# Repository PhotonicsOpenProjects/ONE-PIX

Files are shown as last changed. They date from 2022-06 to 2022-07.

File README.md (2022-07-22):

<p align="center">
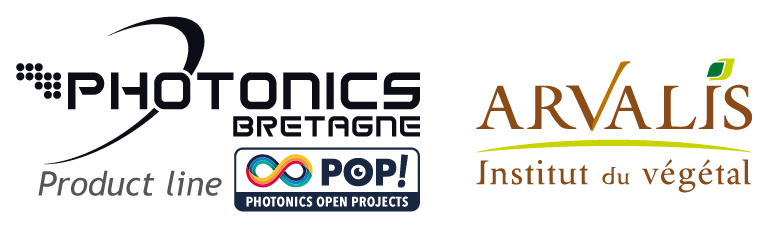
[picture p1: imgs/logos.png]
logos

</p>

# ONE-PIX kit project   #
## Introduction 

The ONE-PIX kit is an hyperspectral camera using single pixel imaging principle to measure hypercubes in the visible region. It can be enhanced towards the infrared region. This modular kit can be used with different spectrometers and optical elements for the collection. To date, it can measure scenes exposed to ambient light, but it has been primarily tested and developed for use in dimly lit indoor environments.

This kit is ideal for getting started with hyperspectral imaging or single pixel imaging. Thus it is a tool for teachers and students to discover non conventional imaging. It is also an economic tool to produce low cost hypercubes of tailored scenes or to reproduce academical results within the robotic vision field. 
To learn more about single pixel imaging theory used for hyperspectral imaging, you can read our [article. ](https://www.ncbi.nlm.nih.gov/pmc/articles/PMC7070961/)

This kit was developed with the primary need in mind to be able to be assembled on a standard fablab with laser cutting. Little wiring (all low voltage) and no soldering is required. You should find a fablab in your neighbourhood capable (and enthusiastic) of helping you build this cool instrument, especially if they can have some fun with it afterwards.

### Working principle

The ONE-PIX kit contains a video projector and a fibered spectrometer with superimposed fields of view. Both are connected and controlled by a Raspberry Pi board.
 
<p align="center">
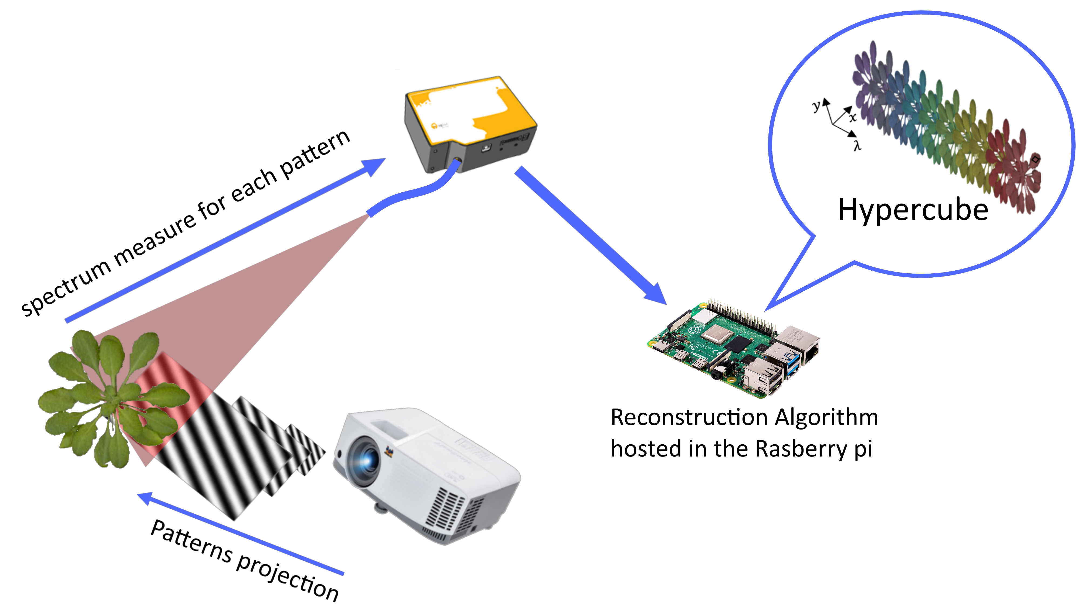
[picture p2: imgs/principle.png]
ONE-PIX principle

</p>

For more information about the single pixel imaging you can go [here](ONE-PIX_soft/doc/Single%20Pixel%20Imaging%20tutorial/Single%20Pixel%20Imaging.ipynb)

ONE-PIX technology involves projecting a series of patterns onto a scene to be imaged. A spectrometer measures the average reflected spectrum of the scene for each projection. An algorithm then reconstructs the hypercube of the scene from all the spectra measured during the acquisition. 
The Raspberry Pi board ensures the synchronization between patterns projections and the spectrometer measurements.
### Architecture of the ONE-PIX kit repository 

The ONE-PIX kit project contains two folders :

- A [hardware build folder](hardware_build) contains all the files and information to build a case containing all the components of the ONE-PIX kit and their 3D printed attachments.
- A [ONE-PIX Software folder](ONE-PIX_soft) contains the scripts and software embedded on the Raspberry Pi and all the information to install and use it properly. 
## Steps to produce one ONE-PIX kit

These followings steps are presented in chronological order to create a ONE-PIX kit. 

### Build your own hardware ONE-PIX kit

Every informations and files to build your own hardware kit are avalaible in the [hardware build folder](hardware_build)

<p align="center">
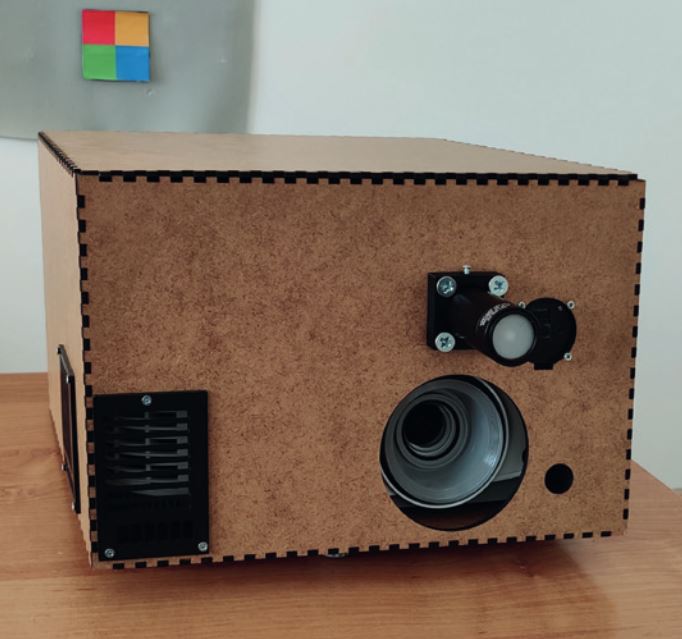
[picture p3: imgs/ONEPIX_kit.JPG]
ONE-PIX kit photo

</p>

This folder contains:

- The [material needed list](hardware_build/materials_needed.pdf) file containing raw materials and equipments needed to build the ONE-PIX kit hardware.
- The [hardware building tutorial](hardware_build/hardware_building_tutorial.pdf) file containing details steps to build the ONE-PIX kit.
- [STL files ready to 3D_printing](hardware_build/STL_file_ready_to_3D_printing) folder containing every files to 3D print components fixation parts of the kit.
- [plans of box sides ready to cut](hardware_build/plan_of_box_sides_ready_to_cut) folder containing every files to  laser cut sides of the ONE-PIX kit case.
- The [CAO files to modify hardware](hardware_build/CAO_files_to_modify_hardware) folder containting the complet CAO of the ONE-PIX kit if you want to adapt the hardware to your application.

> **_NOTE:_** You can also buy a premounted and adapted ONE-PIX kit [here](https://www.photonics-bretagne.com/fr/product/imageur-hyperspectral-one-pix-pop/). 
> Keep in mind that it is also the best way to help us maintaining the forge, integrating contribution and even propose one day industrial implementation of this technology for the broader audience and usage possible.

### Install ONE-PIX software on the Raspberry Pi 

To install the ONE-PIX kit software you need to follow steps discribed in [Readme installation](ONE-PIX_soft/README.md) before measuring hyperspectral images.
For troubleshooting in installation you can go to the [issue section](https://github.com/PhotonicsOpenProjects/ONE-PIX/issues)

###  Measuring and analysing hypercubes 

The software architecture of the ONE-PIX kit offers different ways to measure, reconstruct and analyze hyperspectral images. 

<p align="center">
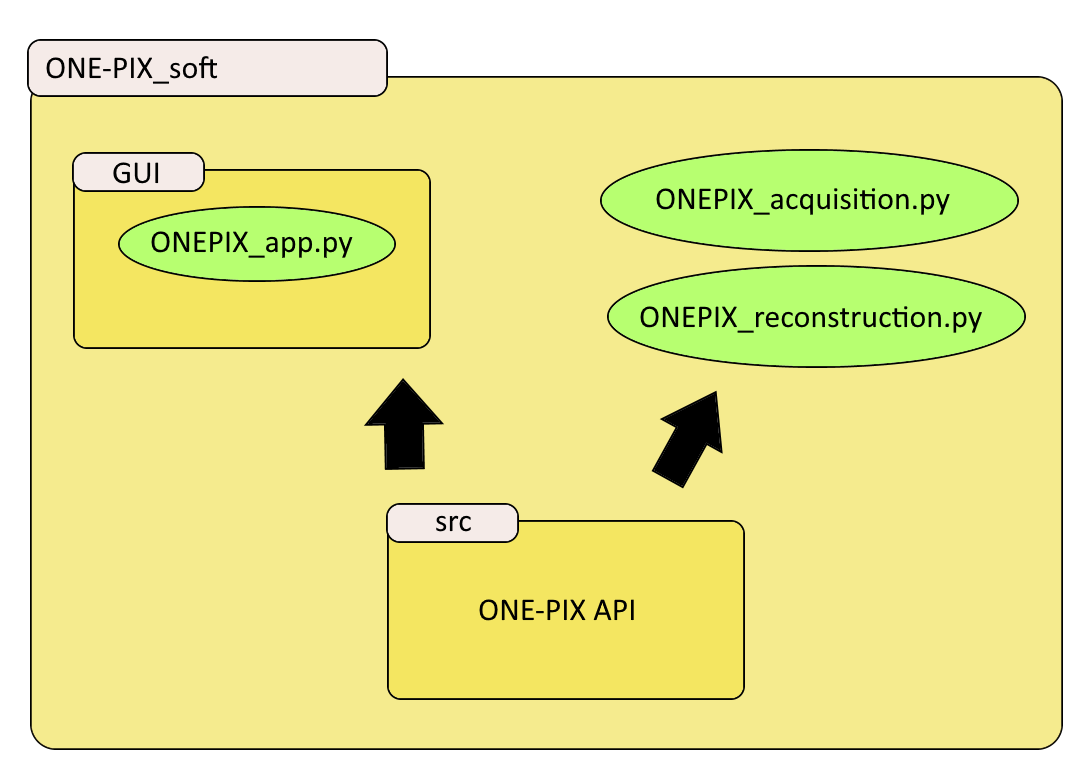
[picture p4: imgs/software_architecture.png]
ONE-PIX software architecture

</p>

- The fastest way to measure and analyze hyperspectral images is to use the [GUI interface](ONE-PIX_soft/doc/ONE-PIX_GUI_user_manual.pdf)
- For more advanced acquisitions,use directly ONEPIX_acquisition.py and ONEPIX_reconstruction.py [Python examples scripts](ONE-PIX_soft) and improve them with using the [API](https://one-pix.readthedocs.io/en/latest/introduction.html).
 
## Contributing 

### Mounting experience

If you use it from a already assemble kit, and do not found a detail on the manual, tell us !
If you assemble it by yourself and found some simpliest or smartest way to do it, please share !
If you encounter difficulties, have suggestions or even just cheers the developpers, do not hesitate again !

### Use Cases

Any questions, pedagogical or in a front of science, very applied or meta-conceptual are interesting for us and other users. A brief description and welcome message on this repository will be greatly apreciated. If we are curious enough we will contact you.

### New functions

As you will rapidly catch-it : this simple set-up has an infinity of potential developements, applications and usages. Feel free to play with it once it works at your place. 
If you find new tricks, feel free to share it with us and the community. We will dedicate ourselves (on the limits of our daily hours) to make the best effort to integrate and promote to the community every contribution with the greater respect to your credits. 

### Your version

If you tried a new sensors, an other mechanical plan, you can freely create your own forks but if you consider it could be usefull to keep consistency with other develepment and insturmental choice, we can discuss on intégrating also , spectormeter wrappers or even more crazy evolution in the main.

## Important remarks

:bulb: **Tip:** Do not forget to have fun... because we had some making it for you !

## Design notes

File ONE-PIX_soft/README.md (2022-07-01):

# Readme for the ONE-PIX software installation #
# Introduction 

The installation of the ONE-PIX software is achievable as the hardware installation is fully completed..
To do so, you can follow the [hardware building tutorial](/hardware_build/hardware_building_tutorial.pdf) .
You can also buy an already premounted ONE-PIX  kit [here](https://www.photonics-bretagne.com/fr/product/imageur-hyperspectral-one-pix-pop/)

This tutorial details all the steps required to install the ONE-PIX software on a Raspberry Pi 4 board. 

# Installing the Raspberry Pi OS on the SD card and remote control

We recommend to use The ONE-PIX with a remote control Desktop.It allow you to run long acquisition in a more automated way. 

<p align="center">
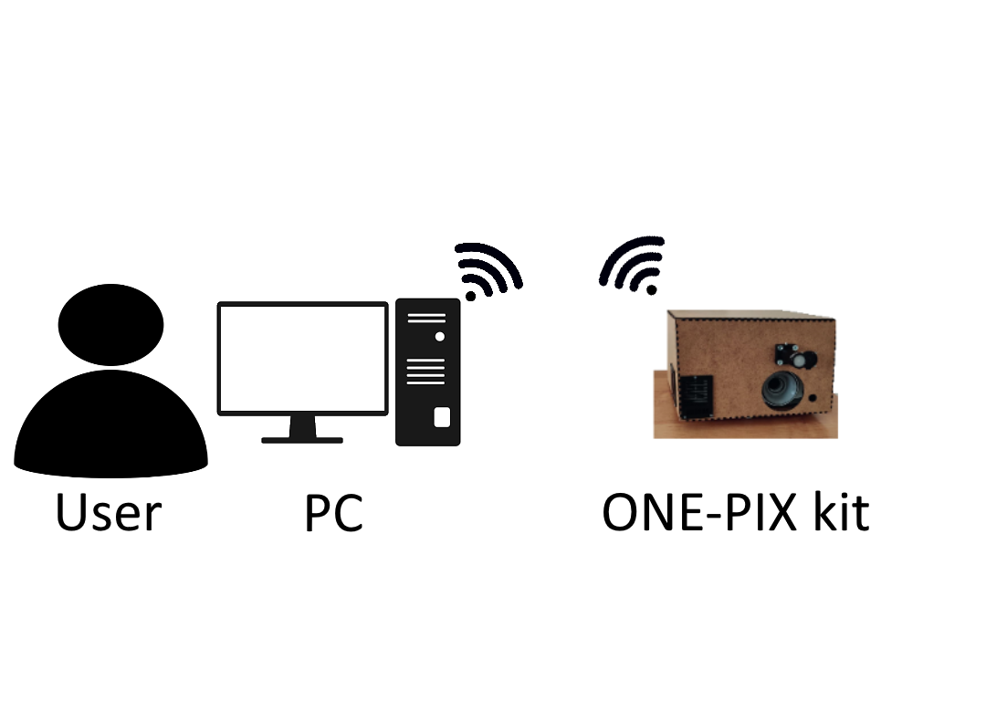
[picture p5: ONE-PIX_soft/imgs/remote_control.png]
remote control

</p>

Here we assume that The ONE-PIX soft was developed to use a raspberry pi with Raspbian OS.
However it possible use directly your PC with python for more advanced performance. 

To install the Raspbian OS on the SD card you can follow steps on this link [here](https://www.raspberrypi.org/documentation/installation/installing-images/ )

To remote control your raspberry pi you can follow this tutorial [here](https://www.realvnc.com/en/blog/how-to-setup-vnc-connect-raspberry-pi/#:~:text=You%20can%20even%20create%20and,will%20be%20able%20to%20connect. )

# ONE-PIX software installation 

## Download git repository

The first step of this installation is to clone the ONE-PIX directory from Github.

From the Raspberry Pi, open a terminal and go to the desktop with the following command line:

```
cd Desktop
```

Download the ONE-PIX software from git 

```
sudo git clone https://github.com/PhotonicsOpenProjects/ONE-PIX.git
```

## Requirements installation

A folder ONE-PIX _soft was created on the desktop.
with the terminal go in this folder 

```
cd Desktop/ONE-PIX/ONE-PIX_soft
```

You need to install Python packages to run ONE-PIX_soft. 
For that, just run the following command:

```
pip install -r requirements.txt
```

## Dependencies installation
More dependencies are requested to use OceanInsight spectrometers (Seabreeze) and the OpenCV library. 

Installing Seabreeze dependencies: 
```
sudo apt-get -y install libglu1
sudo apt-get -y install libaio1 libaio-dev
sudo apt-get -y install libglib2.0-0
sudo apt-get -y install libasound2
sudo apt-get -y install libusb-0.1-4
```

Installing OpenCV dependencies: 

```
sudo apt-get -y install build-essential cmake pkg-config
sudo apt -y install libjpeg-dev libtiff5-dev libjasper-dev libpng-dev
sudo apt -y install libavcodec-dev libavformat-dev libswscale-dev libv4l-dev
sudo apt -y install libxvidcore-dev libx264-dev
sudo apt -y install libfontconfig1-dev libcairo2-dev
sudo apt -y install libgdk-pixbuf2.0-dev libpango1.0-dev
sudo apt -y install libgtk2.0-dev libgtk-3-dev
sudo apt -y install libatlas-base-dev gfortran
sudo apt -y install libhdf5-dev libhdf5-serial-dev libhdf5-103
sudo apt -y install libqt5gui5 libqt5webkit5 libqt5test5 python3-pyqt5
sudo apt -y install python3-dev
```

## Spectrometer rules configuration
You need to configure USB rules to allow data tranferts from your spectrometer.

If the spectrometer used is this [list of tested spectrometer](../ONE-PIX_soft/doc/tested_spectrometers.pdf) follow steps for your model. 

Else, the spectrometer used is not in this list, you need to see [adding a new spectrometer](https://one-pix.readthedocs.io/en/latest/contributing.html#adding-a-new-spectrometer) API section.

### Ocean Insight spectrometers 

To configure Ocean Insight USB rules you need to copy the file the 10-oceanoptics.rules file stored in the [DLL folder](../ONE-PIX_soft/src/DLL) and paste it in the /etc/udev/rules.d folder of the Rapsberry pi.

For that go to the DLL folder

```
cd src/DLL
```

and copy/paste the 10-oceanoptics.rules in /etc/udev/rules.d folder with this command line:

```
sudo cp 10-oceanoptics.rules   /etc/udev/rules.d
```

### Avantes spectrometers

You need to update the /etc/udev/rules.d file of the raspberry pi to fix USB rules for Avantes Spectrometers.

To do so, go to this file with this command line: 
```
cd /etc/udev/rules.d
```
and add text in the file with these lines: 

```
sed -i '13 i SUBSYSTEM=="usb", ATTRS{idVendor}=="1992", ATTRS{idProduct}=="0667", MODE="0666"' 99-com.rules
sed -i '14 i SUBSYSTEM=="usb", ATTRS{idVendor}=="1992", ATTRS{idProduct}=="0668", MODE="0666"' 99-com.rules
sed -i '15 i SUBSYSTEM=="usb", ATTRS{idVendor}=="1992", ATTRS{idProduct}=="0669", MODE="0666"' 99-com.rules 

```
Finally, save and close the rules.d file.

## Activate Raspberry Pi camera 

to use ONE-PIX kit you need to activate the raspberry pi camera  for that go 

Enable SSH,VNC and the camera 

<p align="center">
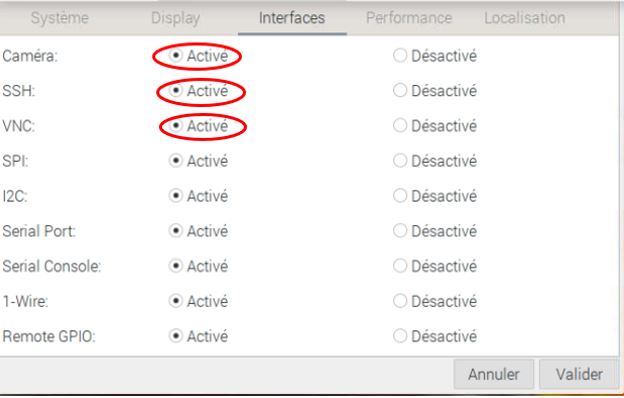
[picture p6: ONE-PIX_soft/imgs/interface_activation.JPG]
interface activation

</p>

## Dual screen configuration
In order to perform ONE-PIX  measurements, it is necessary to set up a second screen dedicated to displaying the patterns to be projected on your scenes.
 
You need to change the boot/config.txt file of the Raspberry Pi to force the double screen stored in DLL folder. 
You need to supress your existing boot/config.txt and replace it by  preconfiguring config file stored in the[DLL folder](../ONE-PIX _soft/src/DLL).
For that use these command lines : 
```
sudo rm /boot/config.txt
sudo cp config.txt /boot
```
# Finalisation and checking of the installation

First, shutdown the Raspberry Pi and replug in the hardware benchtop. 
Then, plug the mini HDMI on the HDMI1 port.  
Power on the projector and the Raspebrry Pi board. 
Remote control your Pi with your computer.

Now, you need to configure screen display. For that, go in the screen configuration menu:

<p align="center">
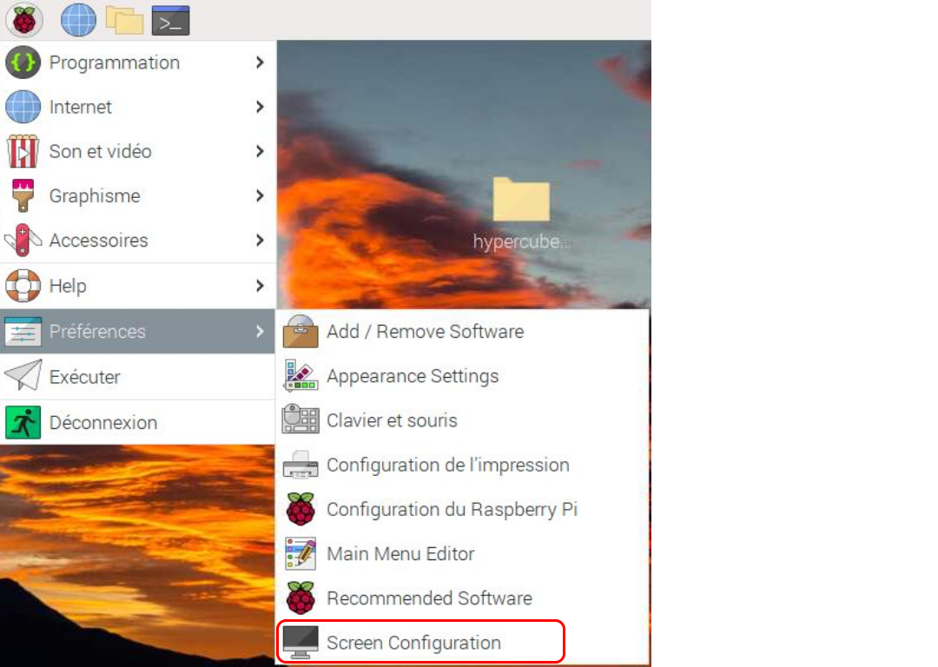
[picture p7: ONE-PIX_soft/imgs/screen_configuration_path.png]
screen configuration menu path

</p>

This window will pop up:

<p align="center">
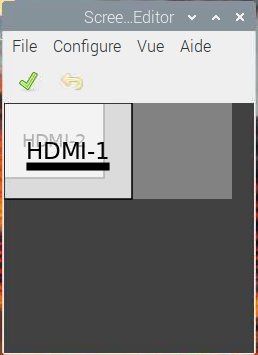
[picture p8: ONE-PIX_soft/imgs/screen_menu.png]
screen configuration menu

</p>

The HDMI1 and HDMI2 are superimposed. You need to grab HMDI 2 at the right of HDMI 1 with the mouse. 

<p align="center">
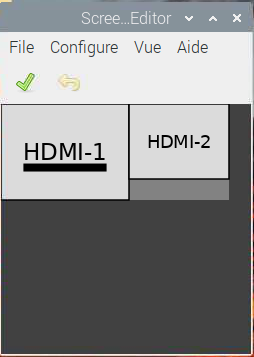
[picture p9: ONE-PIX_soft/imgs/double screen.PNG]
double screen

</p>

Now with VNC Viewer you can see two screens. The first one is the screen of the Raspberry
Pi desktop and the second is the screen of the projector. 

set the resolution of the screen 1 with 1024x768 pix and the screen 2 in 600x800pix. 

click one the green ticks to validate changes.

:warning: **Warning:** For long acquisition it may be necessary to deactivate the sleepmode. you can follow this [tutorial](https://pimylifeup.com/raspberry-pi-screensaver/)

<p align="center">
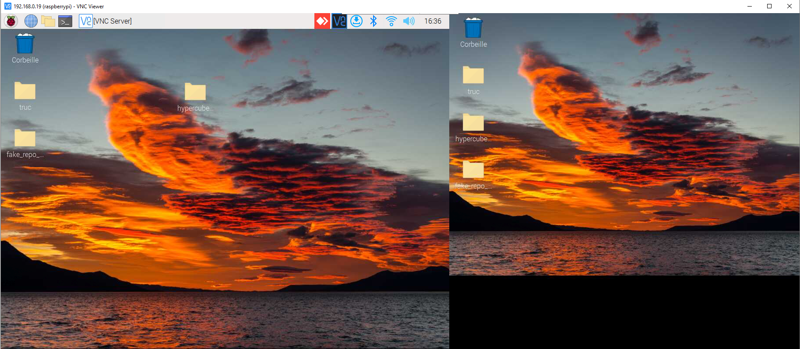
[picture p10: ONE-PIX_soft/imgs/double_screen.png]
vnc vnc viewer double screen

</p>

The installation is now complete. 
Now you can follow the [tutorial measure hyperspectral image](/ONE-PIX_soft/doc/tutorial_measure_hyperspectral_image.pdf) to measure your first hyperspectral datacube !

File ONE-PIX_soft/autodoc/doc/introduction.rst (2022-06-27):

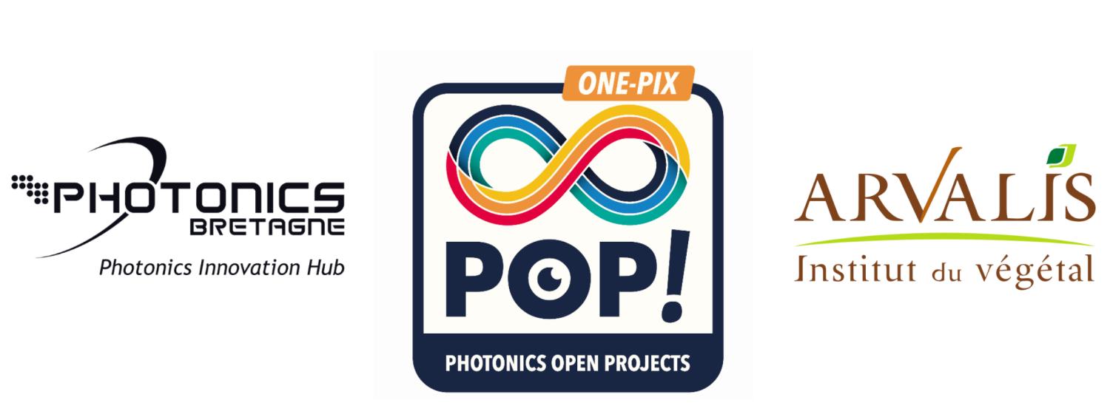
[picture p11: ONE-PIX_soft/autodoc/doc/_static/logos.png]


============
Introduction
============

The ONE-PIX kit is a low-cost single-pixel hyperspectral imaging education kit. This module is fully available on Github (see `here <https://github.com/IanHarvey/bluepy/>`_)
The current implementation has been developed in Python 3 and tested on a Raspberry Pi 4 8 Go, running Raspbian 11 (bullseye), but should also work with Windows or Ubuntu on most computers.

Motivations
------------
As the various spectral imaging technologies are relatively very expensive, we want to popularise the use of these new cutting-edge technologies. Thus, this kit aims to allow anyone to design their own kit or to order one from Photonics Bretagne.
As this research topic remains very broad, a Github repository allows to share all the contributions made within a community dedicated to single-pixel hyperspectral imaging.

This package is intended to provide:
--------------------------------------------

- Python scripts for interfacing the kit.
- Acquisitions and reconstructions scripts implementing various compressed imaging methods 
- Analysis tools to make use of the measured datacubes 



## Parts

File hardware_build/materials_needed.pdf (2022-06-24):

Type of item | item | quantity | comments
Component | Modified PA503S viewsonic videoprojector | 1 | For an optimal performance the hspi kit need a video projector with a modified optical chain. You can contact us to buy one here. (https://www.photonics-bretagne.com/en/perfos-rto/products/services/)
| Rasbperry pi 4B+ (8Go Ram) model | 1
| micro SD card 64 Go with SD adaptator | 1
| USB key | 1
| Raspberry pi camera | 1
| Optical fiber | 1
| SM1 thorlabs tube | 1
| Divergent lens | 1
| SM1 SMA Thorlabs connector | 1

Raw material

MDF plank with tickness 3 mm | 1200*1200
mm² | Depend of the dimension of the laser cutter CNC
Filament PLA | 30 meters
Wires | Mini HDMI/HDMI cable | 1
| Raspberry pi camera wire | 1 | CSI cable 15 pin
Lenght >30 cm
C13 Alimentation cable of the video projector | 1
Alimentation cable of the raspberry pi 4B+ model | 1

Type of item | item | quantity | comments
Screws and nuts | M6 screws | 4
| M6 nuts | 4
| M4 screws | 3
| M3 screws | 16
| M3 nuts | 16
| M2.5 screws | 11
| M2.5 nuts | 4
| M2 screws | 4
| M2 nuts | 4
Equipment needed | Laser cutter cnc | | Tested with the laser cutter appolo 600 of the Roannes fablab
| 3D printer | | Tested with prusa MK3S and prusa mini
| Phillips screwdriver
| mallet

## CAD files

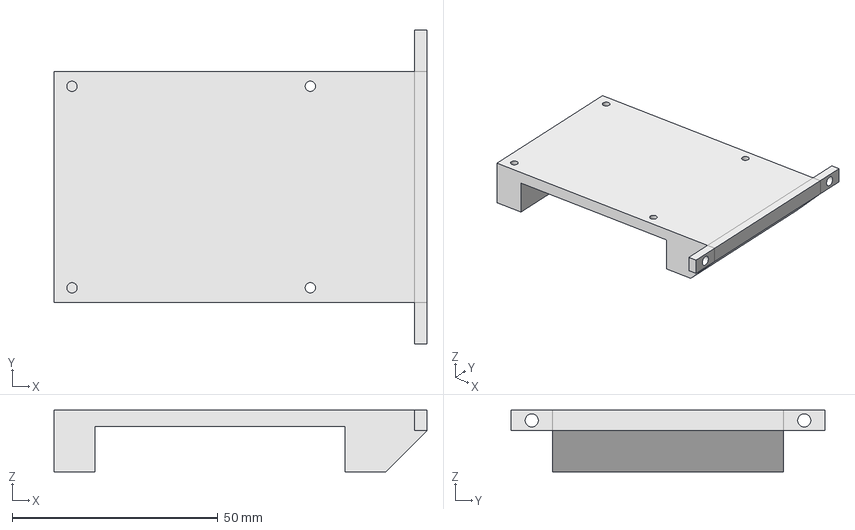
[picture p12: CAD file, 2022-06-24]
hardware_build/CAO_files_to_modify_hardware/Freecad and step files of all components/Raspberry pi fixation part.FCStd
90.8 x 76.3 x 15.0 mm

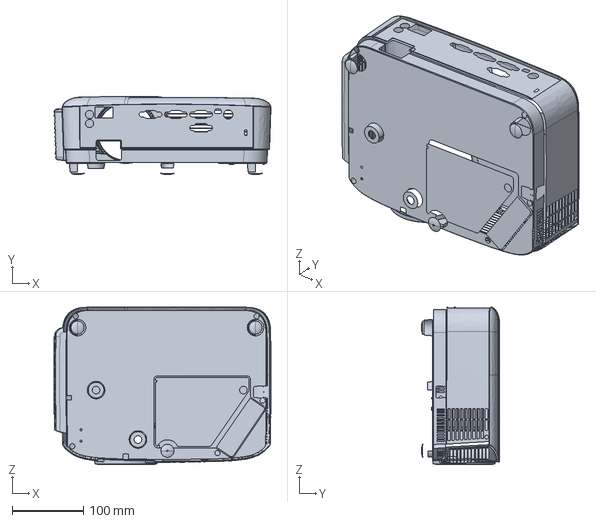
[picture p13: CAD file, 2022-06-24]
hardware_build/CAO_files_to_modify_hardware/Freecad and step files of all components/step files of components/PA503Svideo projector model.stp
304.9 x 110.0 x 221.5 mm

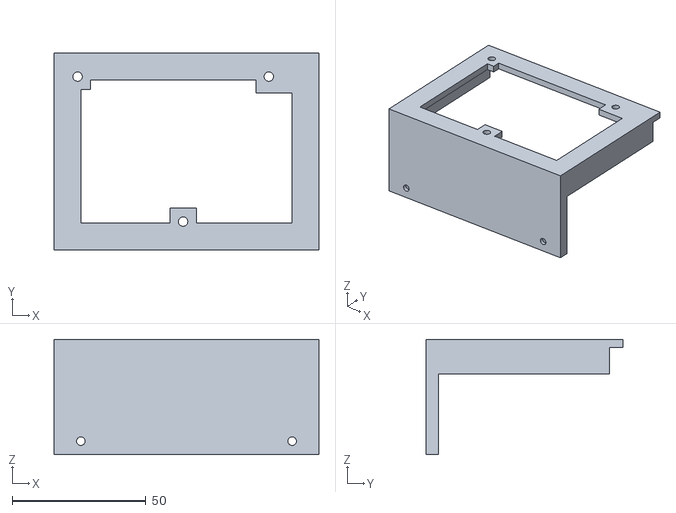
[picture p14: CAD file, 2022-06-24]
hardware_build/STL_file_ready_to_3D_printing/spectrometers fixation parts/Ocean optics Flame fixation part.stl
98.9 x 73.5 x 43.0

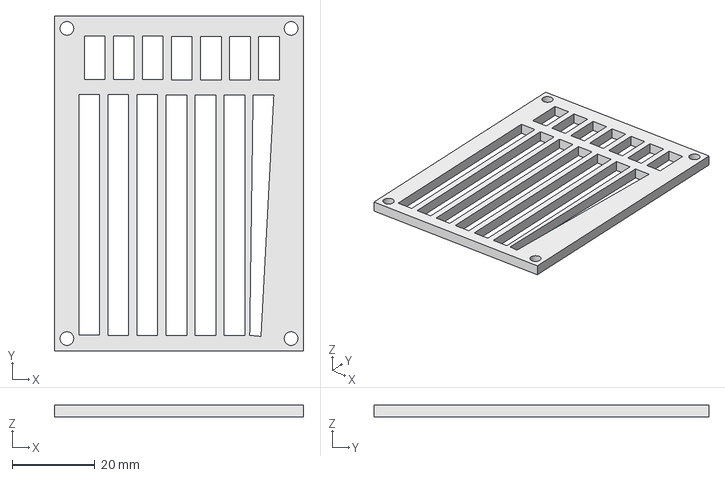
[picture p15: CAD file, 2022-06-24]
hardware_build/CAO_files_to_modify_hardware/Freecad and step files of all components/Right side aeration part.FCStd
60.0 x 80.8 x 3.00 mm

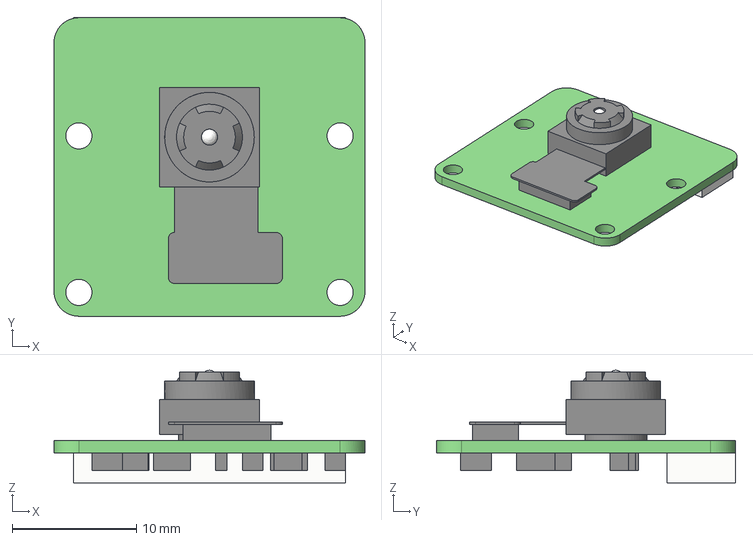
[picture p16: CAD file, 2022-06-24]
hardware_build/CAO_files_to_modify_hardware/Freecad and step files of all components/step files of components/RPi_Camera_Module_v2.igs
25.0 x 24.0 x 9.05 mm

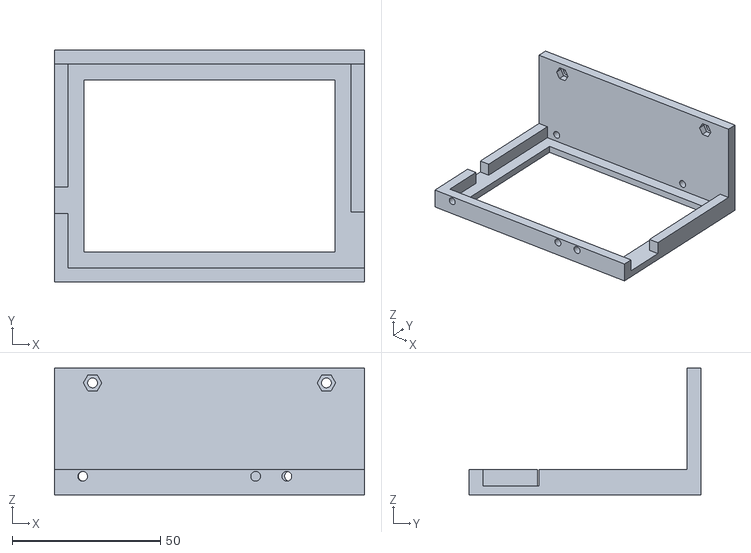
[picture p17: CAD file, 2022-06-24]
hardware_build/STL_file_ready_to_3D_printing/spectrometers fixation parts/avantes spectrometer fixation part.stl
104.6 x 78.1 x 42.8

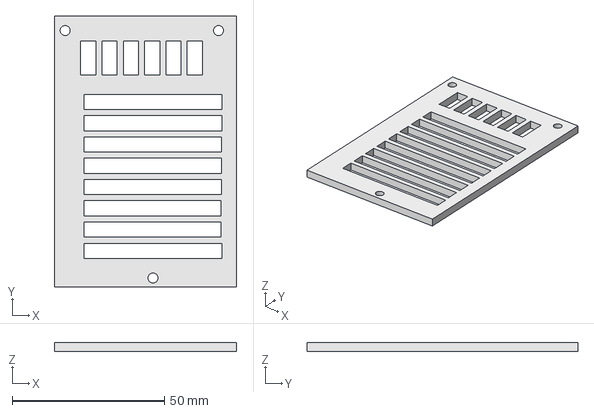
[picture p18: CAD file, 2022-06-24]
hardware_build/CAO_files_to_modify_hardware/Freecad and step files of all components/Front side aeration part.FCStd
59.9 x 89.1 x 3.00 mm

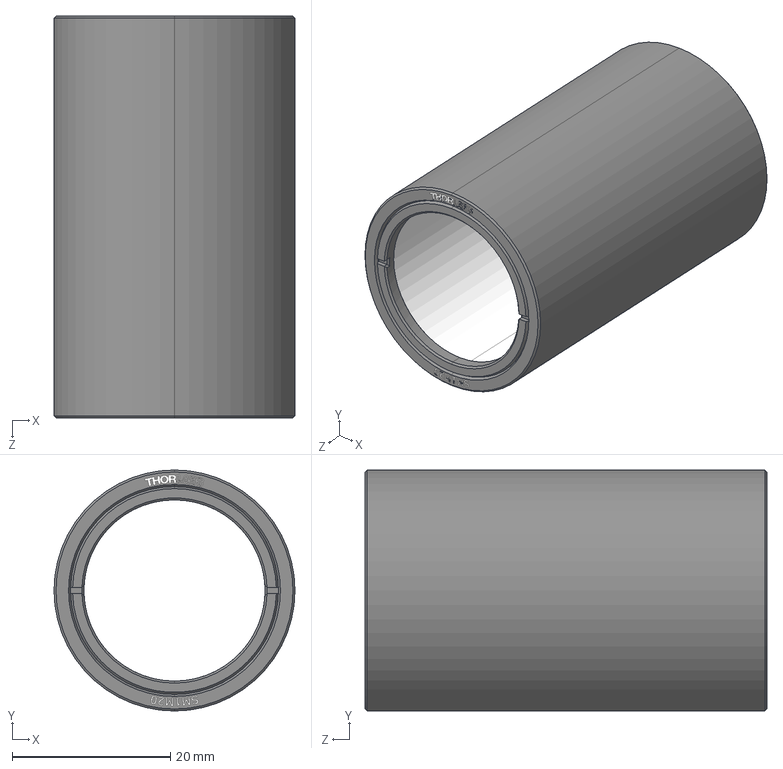
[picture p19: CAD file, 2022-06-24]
hardware_build/CAO_files_to_modify_hardware/Freecad and step files of all components/step files of components/optical_tube.step
30.5 x 30.5 x 50.8 mm

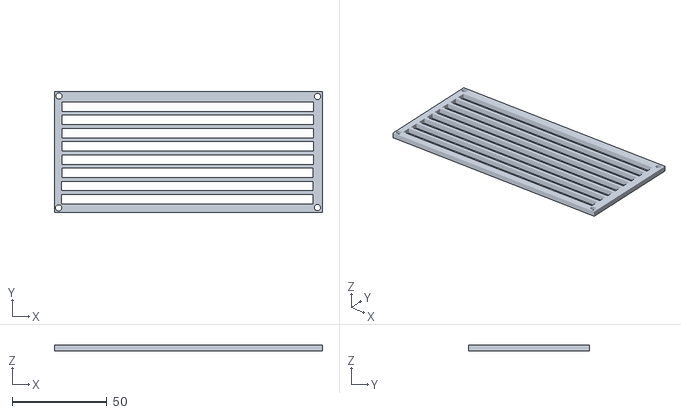
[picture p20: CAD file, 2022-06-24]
hardware_build/STL_file_ready_to_3D_printing/right side aeration part.stl
141.6 x 63.8 x 3.00

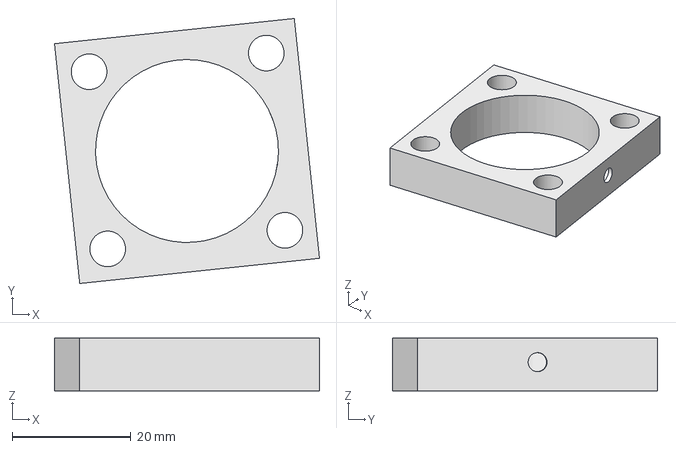
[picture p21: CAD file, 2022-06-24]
hardware_build/CAO_files_to_modify_hardware/Freecad and step files of all components/optical tube fixation part.FCStd
44.6 x 44.6 x 8.90 mm

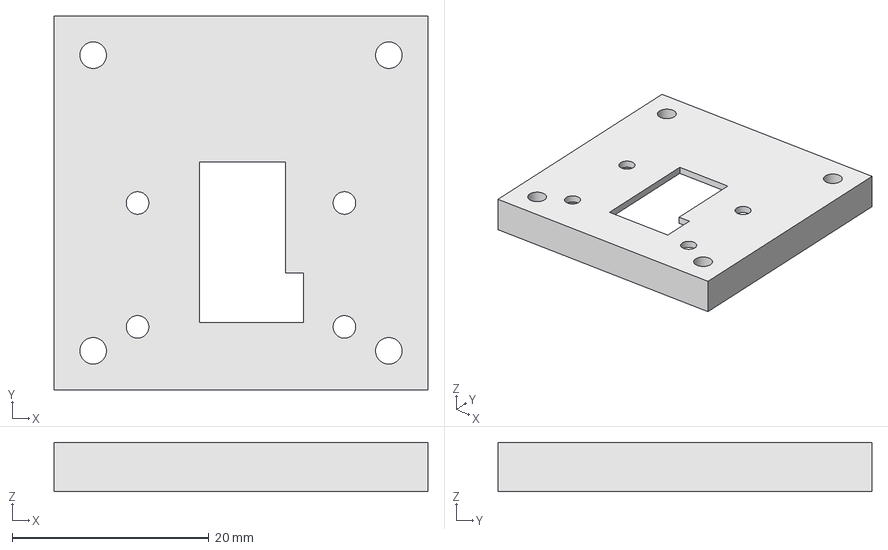
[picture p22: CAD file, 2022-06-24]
hardware_build/CAO_files_to_modify_hardware/Freecad and step files of all components/Raspberry pi camera fixation part.FCStd
38.0 x 38.0 x 5.00 mm

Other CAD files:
hardware_build/STL_file_ready_to_3D_printing/Rasberry pi fixation part.stl
hardware_build/STL_file_ready_to_3D_printing/left side aeration part.stl
hardware_build/CAO_files_to_modify_hardware/Freecad and step files of all components/Avantes spectrometer fixation part.FCStd
hardware_build/STL_file_ready_to_3D_printing/front side aeration part.stl
hardware_build/STL_file_ready_to_3D_printing/optical tube fixation parte.stl
hardware_build/STL_file_ready_to_3D_printing/raspberrypi camera fixation part.stl
hardware_build/CAO_files_to_modify_hardware/Freecad and step files of all components/Left side aeration part.FCStd
hardware_build/CAO_files_to_modify_hardware/Freecad and step files of all components/OceanInsight Flame spectrometer fixation part.FCStd

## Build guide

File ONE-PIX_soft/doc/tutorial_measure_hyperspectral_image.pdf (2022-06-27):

## Introduction

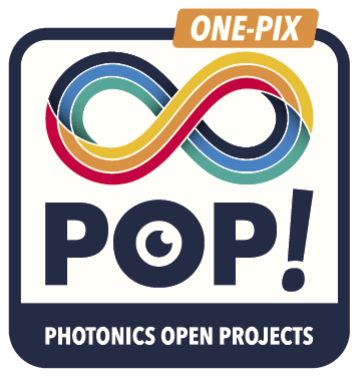
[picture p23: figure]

Her we presume that you follow steps to build or buy the hardware implementation of the ONE-PIX kit and install the ONE-PIX software on your raspberry pi.
If it’s not the case you can follow theses steps :
- Hardware building tutorial
- Readme installation

### Software description

ONE-PIX software is stored on the Raspbian Desktop of the Raspberry pi in the "ONE-PIX/ONE-PIX_soft" folder.
The software allows to control and synchronize every component of the ONE-PIX kit to launch hypercubes acquisitions and analyse them. There is two way to use the ONE-PIX software:

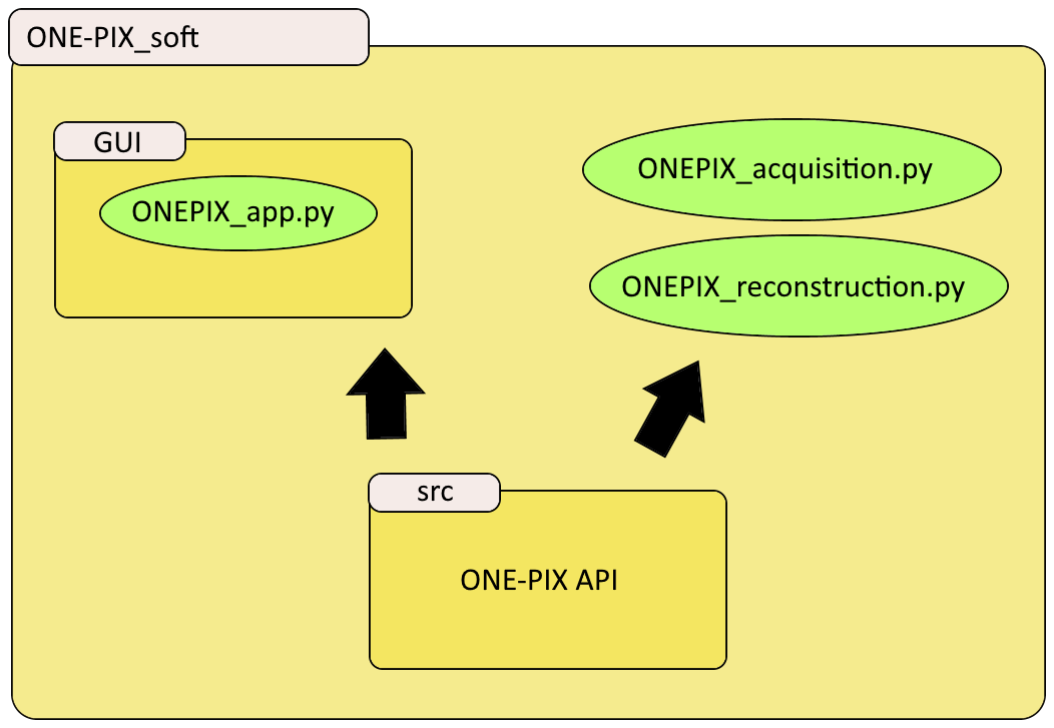
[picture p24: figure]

The easiest way is to use the Python GUI interface (see section 5 and 6 to use it). It allows to run acquisition and analyze it without writing a single line of code. The advantage of using GUI interface is its simplicity. However, its use does not allow more experienced users to do more advanced analysis. For these users, it will be necessary to use scripts adapted to their needs. Two scripts have already been implemented and stored here to get started :

- ONEPIX_acquisition.py
- ONEPIX_reconstruction.py

Using your own Python script implied to have programming skills in Python but allow more analytical possibility and more modularity for acquisitions.
In both cases, GUI interface and script examples are based on the ONE-PIX API. The API consists of several Python libraries containing all functions needed to launch acquisition reconstruct and analyse hypercubes. The documentation of this API can be found here. (https://one-pix.readthedocs.io/en/latest/introduction.html)

### Hardware installation

1) Place the ONE-PIX kit horizontally on stable surface at the recommended working distance of 50 cm of the scene to measure.

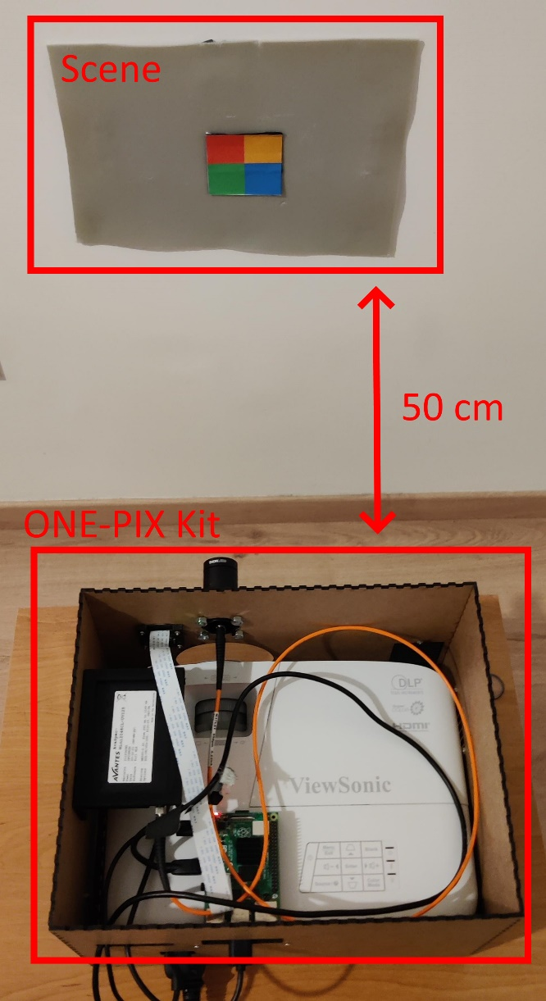
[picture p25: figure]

2) Powering the projector: connect C13 alimentation cable to the projector at the back side of the ONE-PIX kit (see point 1 section 2.3 mechanical view) and powering it.

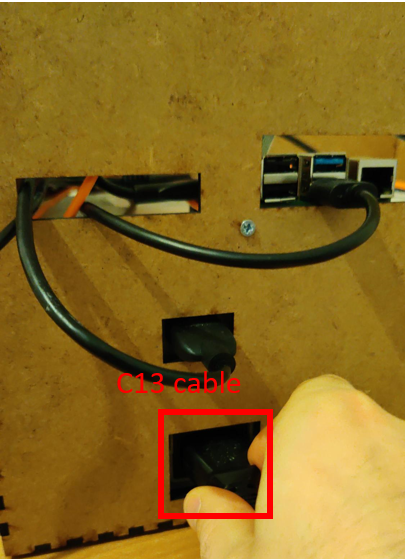
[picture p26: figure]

3) When you see the projection of the projector on the scene powering the Raspberry pi cable and remote control it with VNC viewer.

You will see it:

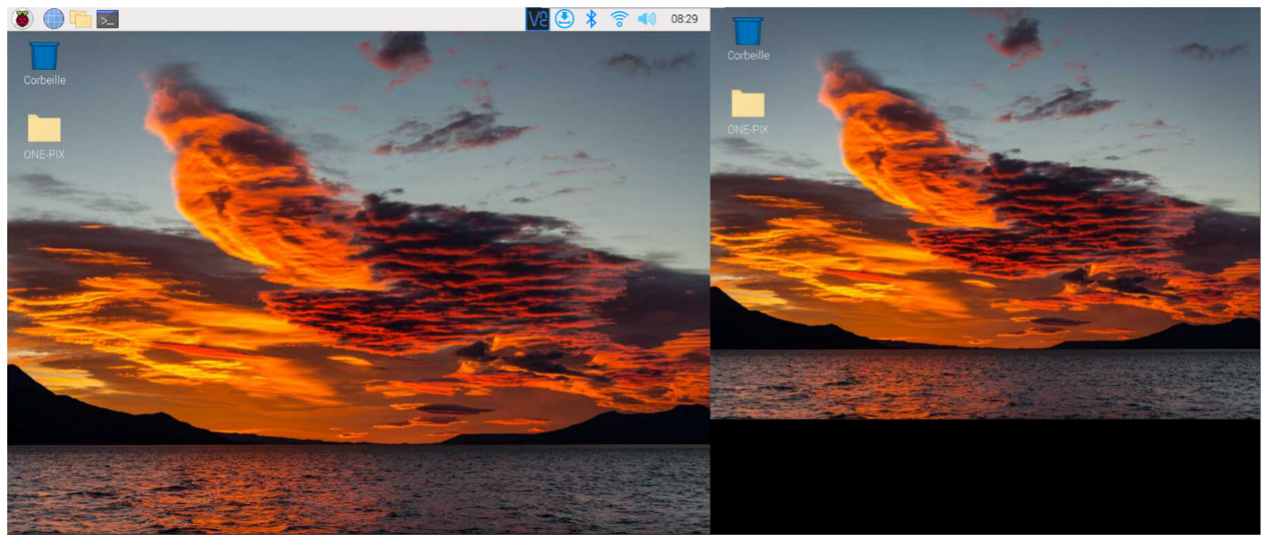
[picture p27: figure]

4) Open the top side of the ONE-PIX test and use the ring to adjust focus and zoom on the scene to see clearly the projected desktop of the pi on the scene.

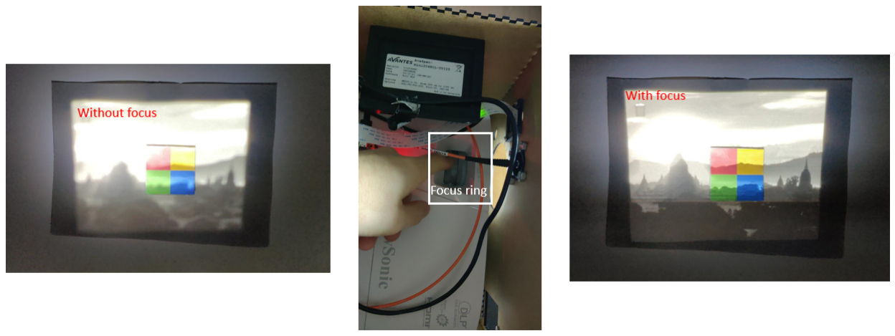
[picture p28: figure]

5) Close the top side of the ONE-PIX kit

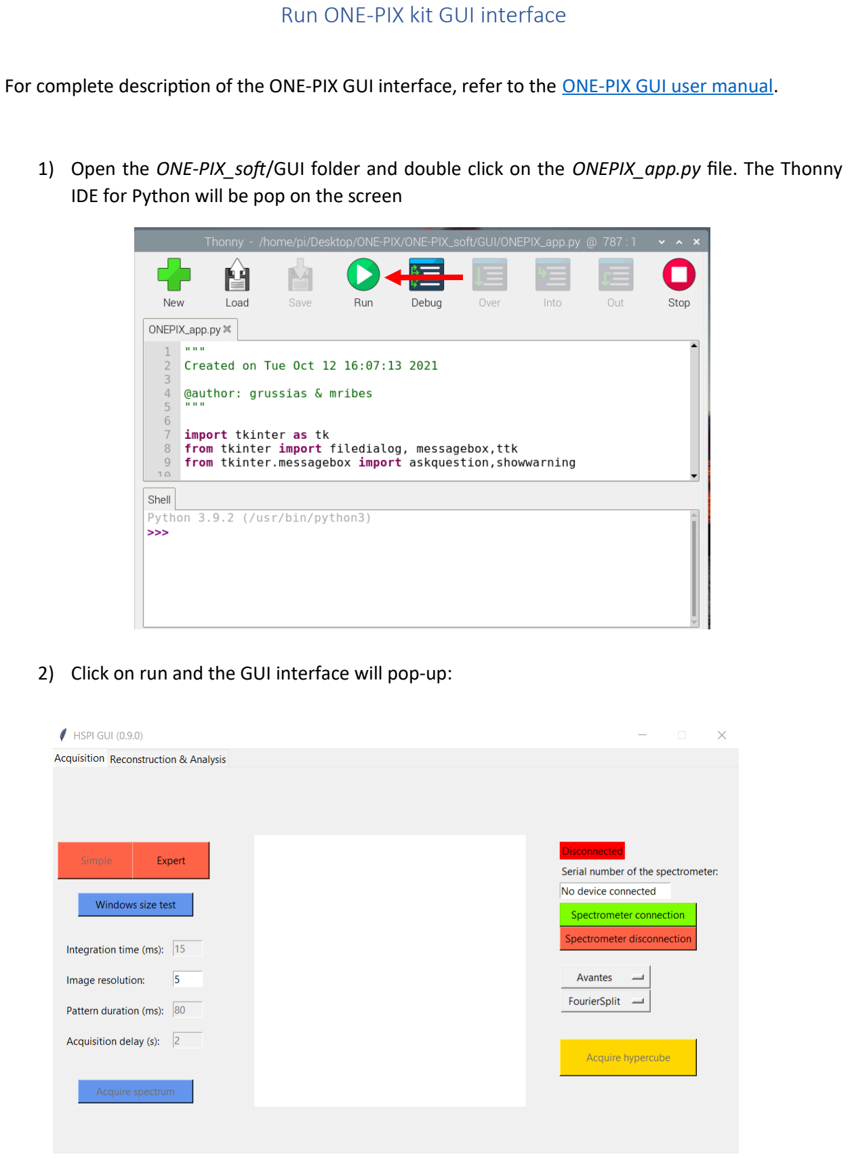
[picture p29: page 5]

### Run ONE-PIX kit GUI interface

For complete description of the ONE-PIX GUI interface, refer to the ONE-PIX GUI user manual.

1) Open the ONE-PIX_soft/GUI folder and double click on the ONEPIX_app.py file. The Thonny IDE for Python will be pop on the screen
2) Click on run and the GUI interface will pop-up:

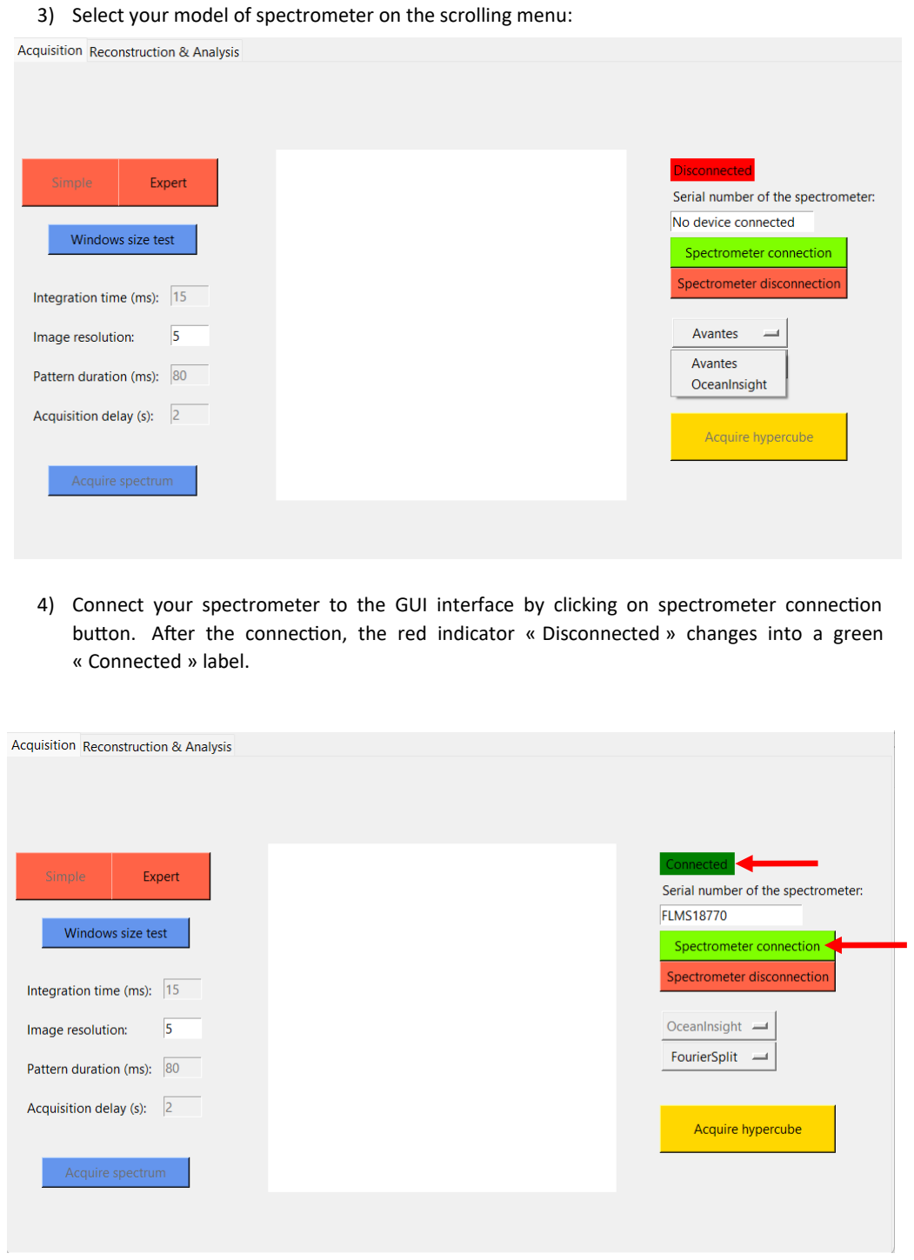
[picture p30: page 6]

3) Select your model of spectrometer on the scrolling menu:
4) Connect your spectrometer to the GUI interface by clicking on spectrometer connection button. After the connection, the red indicator « Disconnected » changes into a green « Connected » label.

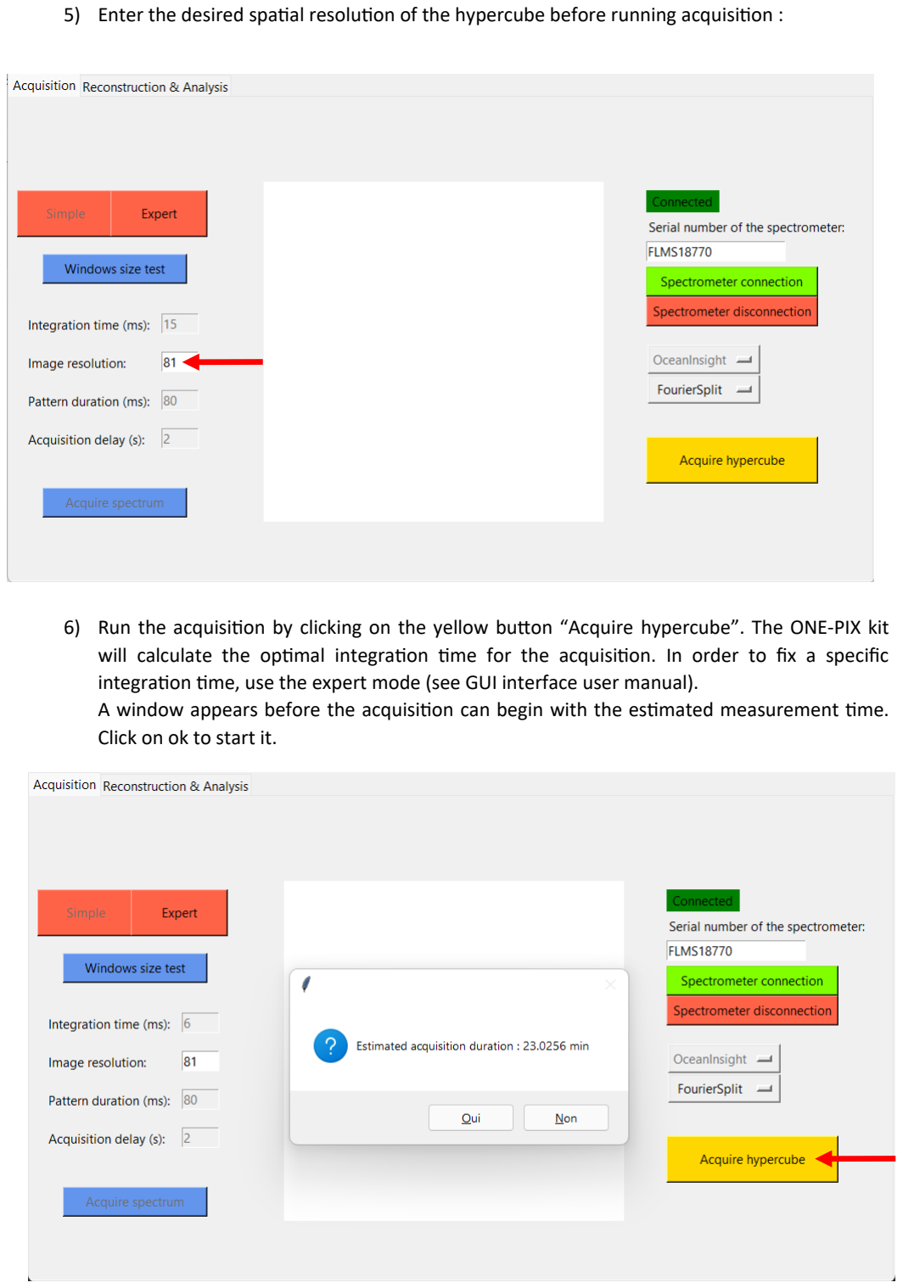
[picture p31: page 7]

5) Enter the desired spatial resolution of the hypercube before running acquisition :
6) Run the acquisition by clicking on the yellow button “Acquire hypercube”. The ONE-PIX kit will calculate the optimal integration time for the acquisition. In order to fix a specific integration time, use the expert mode (see GUI interface user manual).
A window appears before the acquisition can begin with the estimated measurement time. Click on ok to start it.

7) Now the acquisition begins and you can see projected patterns on the scene and on the second screen of the Raspberry pi desktop. Wait the end of the acquisition.

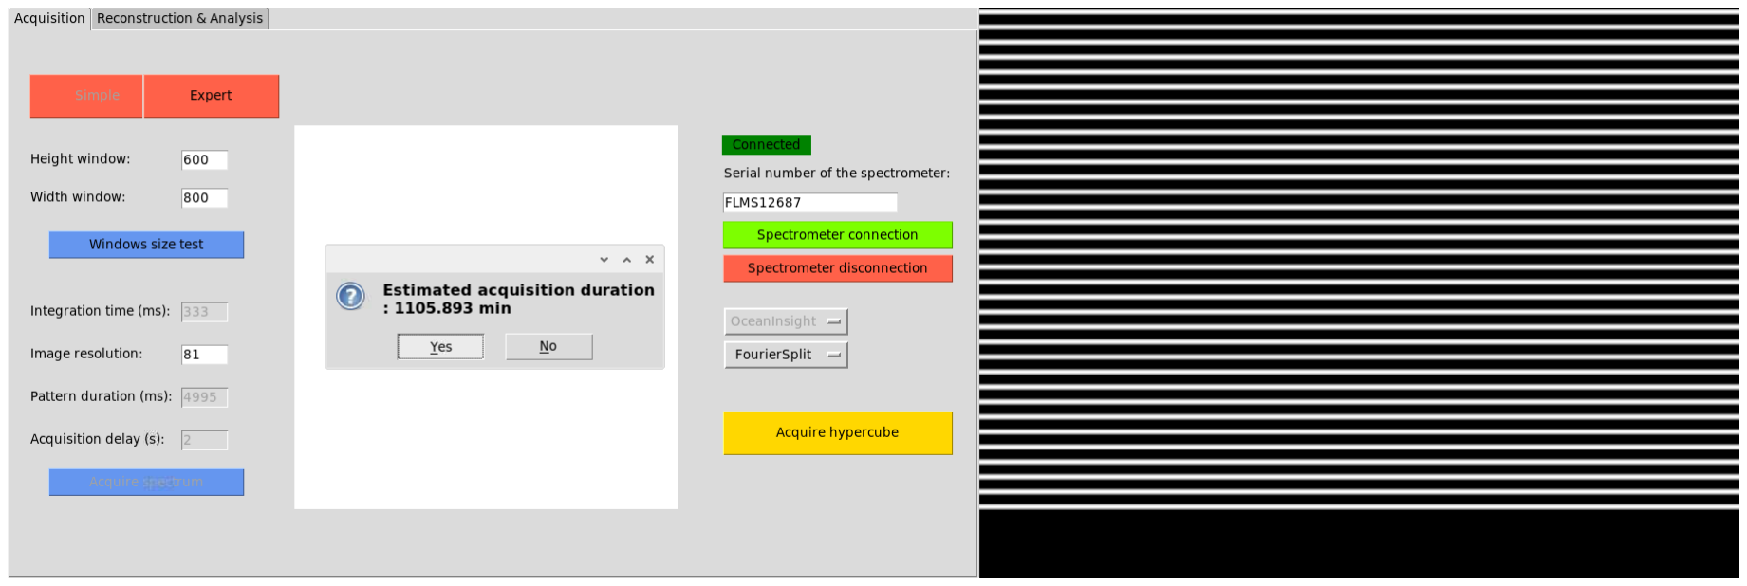
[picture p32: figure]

At the end of acquisition, the ONE-PIX soft save measure in a specific folder. For more information about measures storage see Hypercube format section.
To have more information about visualisation and analyse of hypercube, see the analyse a hypercube section or ONE-PIX GUI user manual.

## Visualize and analyse a hypercube

### Hypercube format storage

After acquisitions, measured data are stored in the Hypercubes folder located at the root of the HSPI_soft folder.

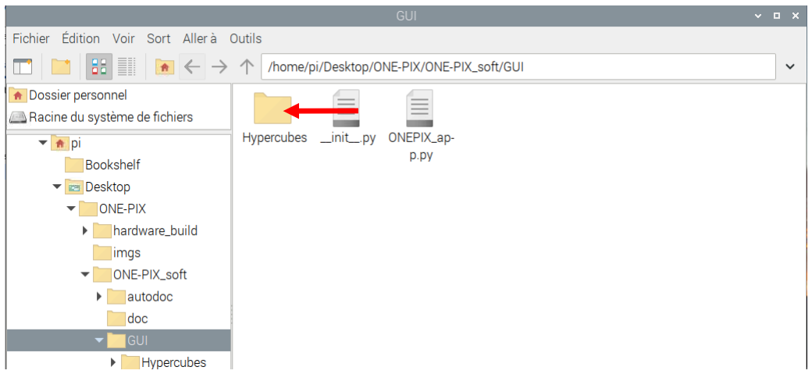
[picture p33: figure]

These data are stored a dedicated folder. The folder name is ONE-PIX_acquisition + date and time of the acquisition :

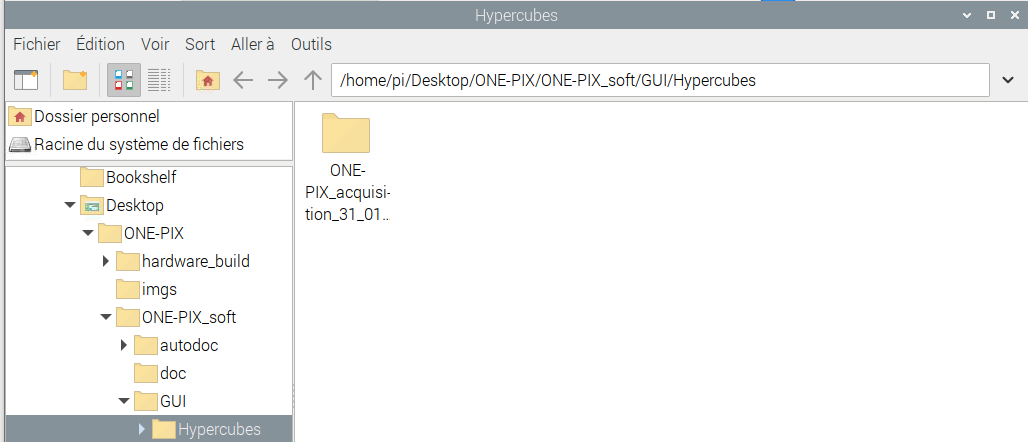
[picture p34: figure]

An acquisition folder contains 5 files :

1: Acquisition parameter +date/time: This text file contains the following acquisition parameters:
- Acquisition method : the single pixel method used to acquire hypercube
- Acquisition time : total duration of the acquisition
-Spectrometer: The serial number of the spectrometer used for the acquisition -Number of projected patterns : the number of projected patterns on the scene -Height of pattern window : Height resolution in pixels of the projected pattern -Width of pattern window : Width resolution in pixels of the projected pattern

-Dark pattern duration : the pause time before the acquisition run -Integration time : integration time of the spectrometer

2: Pattern_order + date/time: NumPy file containing a list of chronological spatial frequency. 3: RGBcam +date/time: JPEG file containing the RGB image of the scene acquire with the Raspberry pi camera.
4: Spectra + date/time: NumPy file containing spectra corresponding of each projected pattern.
: wavelengths +date/time: NumPy file containing spectra’s associated wavelengths.

### Analyse a hypercube

To visualize in false RGB colours the measured hypercube or analyse it, click on the “Reconstruction & Analysis” widget. For a complete description of the widget, refer to the GUI user manual.

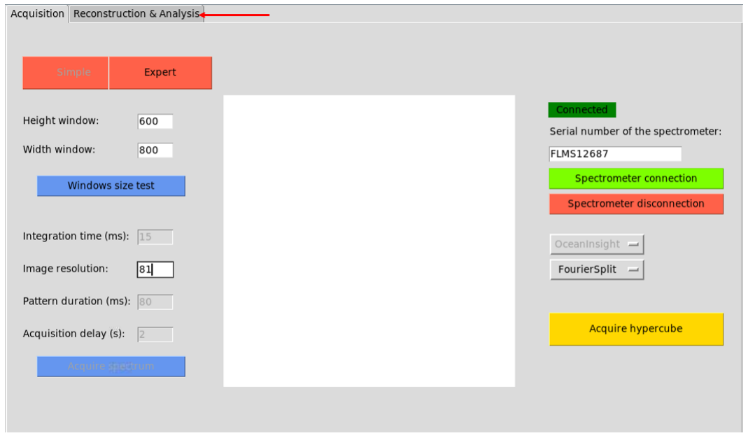
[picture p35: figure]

Load measures on the GUI interface by clicking on the yellow button “Load data”.

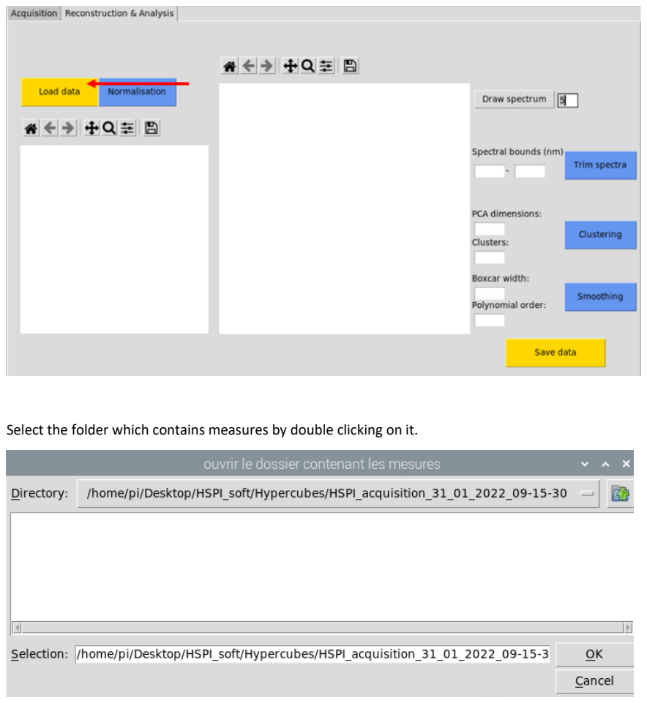
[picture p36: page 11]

Select the folder which contains measures by double clicking on it.

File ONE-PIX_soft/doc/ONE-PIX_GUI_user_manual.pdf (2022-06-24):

## ONE-PIX GUI (1.0.0) user manual :

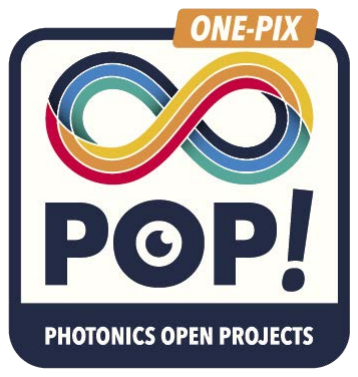
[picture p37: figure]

This GUI allows a user wishing to use ONE-PIX technology to simply make acquisitions and reconstruct them. It consists of two widgets. One to perform hypercube measurements and the other to reconstruct and analyse the results.

- Running Python script « ONEPIX_app.py » creates the graphical interface

Acquisition widget :

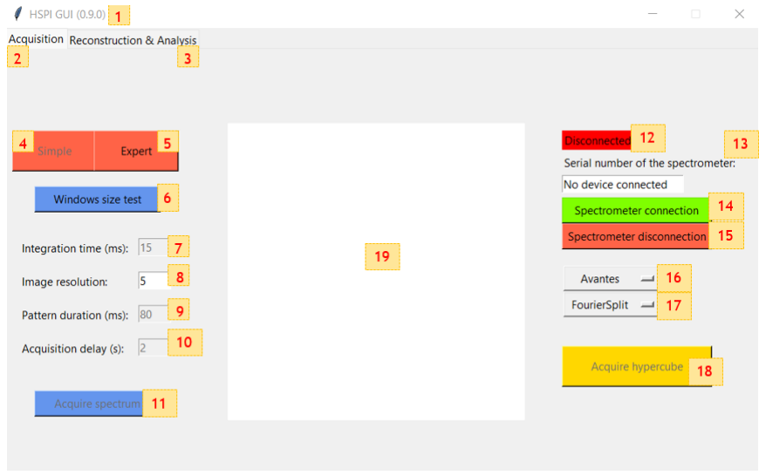
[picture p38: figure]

First of all, it is always necessary to indicate the type of spectrometer[16] used, the pattern basis [17] to be projected, the spatial resolution [8] of the desired hypercube to be reconstructed and to connect the spectrometer by pressing the spectrometer connection button [14].

The Acquisition widget has two operating modes : a simple mode [4] and an expert mode [5].

The simple mode allows measurements to be made automatically without worrying about measurement parameters by pressing the Acquire Hypercube button [18].

Once all the parameters have been determined, a window is displayed to show an estimate of the duration of such a measurement.

If this duration is too long, it is possible to reduce it by decreasing the initial spatial resolution requested or by changing the acquisition parameters by switching to the expert mode.

By clicking on the expert mode, the inputs are unlocked and it is thus possible to modify the measurement parameters manually.

- The integration time [7] is that of a unit measurement made by the spectrometer expressed in milliseconds. In order to manually determine a relevant integration time, it is possible to display any Fourier pattern by choosing its resolution with the Windows size test button [6]. In order to optimise the measurement in terms of signal-to-noise ratio, an integration time should be chosen so that the intensity of the maximum value of the measured spectrum is as close as possible to 40000 counts. However, if this involves too long an acquisition time, it is possible to make trade-offs between SNR and acquisition time.
- The Acquire spectrum [11] button is used to measure a spectrum that will be displayed in the graphics area.
- Pattern duration [9] is the display time of each pattern. This duration must be greater than the integration time and preferably greater than 80 ms. The spectrometer measures on running mode during the acquisitions so that each spectrum measured during the pattern duration can be averaged.
- Finally, the acquisition delay [10] is a delay before running an hypercube acquisition.
- Select the Acquire hypercube [18] button to start the acquisition.

Reconstruction & Analysis widget :

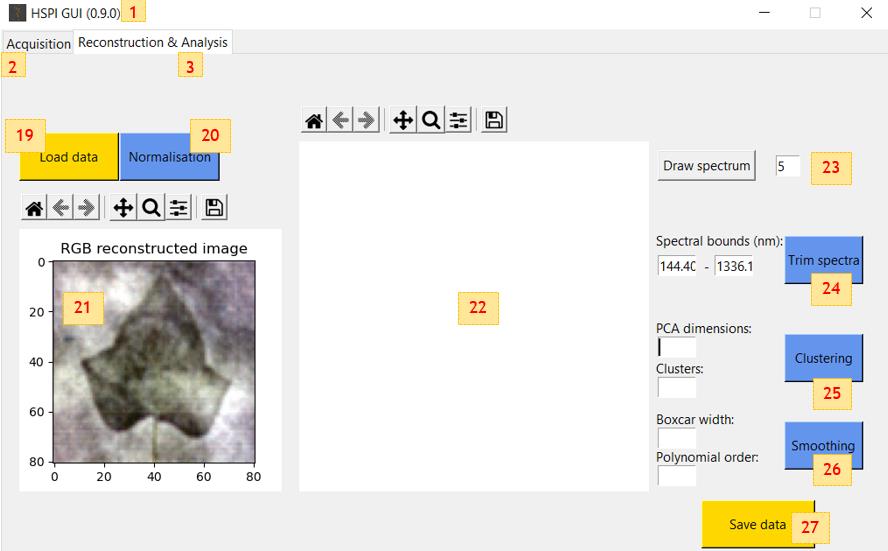
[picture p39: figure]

- By clicking on the Load data button [19], a message box ask if the data to load were already analysed using this app or not. Then a window opens to select the folder containing the hypercube data to be reconstructed for raw data or a «. npy » file containing a dictionnary including analysed data. Finally, a preview of the hypercube appears in RGB format in the graphical area [21].
- The Normalisation button [20] is used to perform a relative reflectance normalisation with respect to the average of a user-selected area of pixels in the image. a window opens and allows you to select the two opposite corners of an area of the hypercube. In order to normalise the hyperspectral data correctly, it is advisable to use calibrated reflectance surfaces.
- On the right side of the interface, it is possible to measure a user-defined number of spectra of the hypercube with the Draw spectrum button and the associated entry [23]. A window displaying the RGB image opens and allows the user to click on the pixels whose spectra they wish to view.
- Clustering button [25] allows to realize classification of the hypercube using kmeans algorithm on principal component of the principal components analysis. To learn more see https://scikitlearn.org/stable/modules/generated/sklearn.decomposition.PCA.html (https://scikit-learn.org/stable/modules/generated/sklearn.decomposition.PCA.html)
- Smoothing button [26] allows to smooth spectra of a whole hypercube using Savitzky-Golay filter. See more at : https://docs.scipy.org/doc/scipy/reference/generated/scipy.signal.savgol_filter.html

- Finally, it is possible to save hyperspectral data using button [27]. RGB images, clustered images and spectra can be directly saved using diskette icons of graphical areas [21] and [22] or from their matplotlib window.

Note : To go further in the normalisations and analyses of the measured hypercubes, it is necessary to use Python scripts and functions in command line.

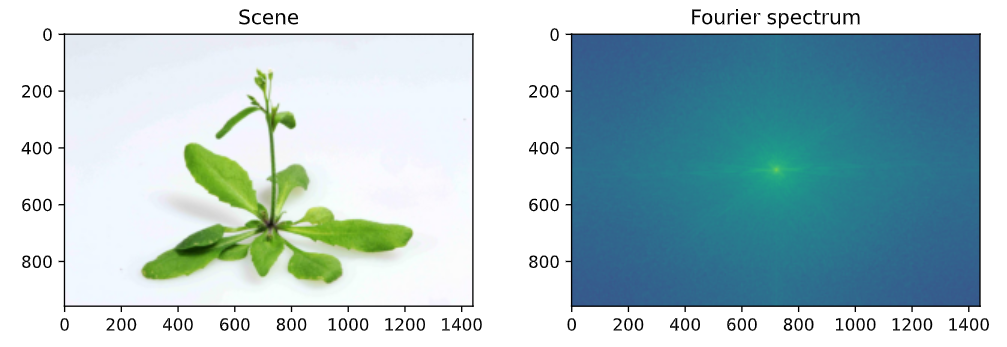
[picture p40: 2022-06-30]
ONE-PIX_soft/doc/Single Pixel Imaging tutorial/fft2.png

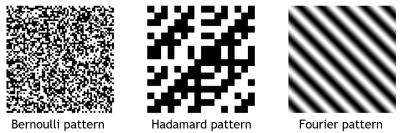
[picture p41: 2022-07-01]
ONE-PIX_soft/doc/Single Pixel Imaging tutorial/patterns_examples.png

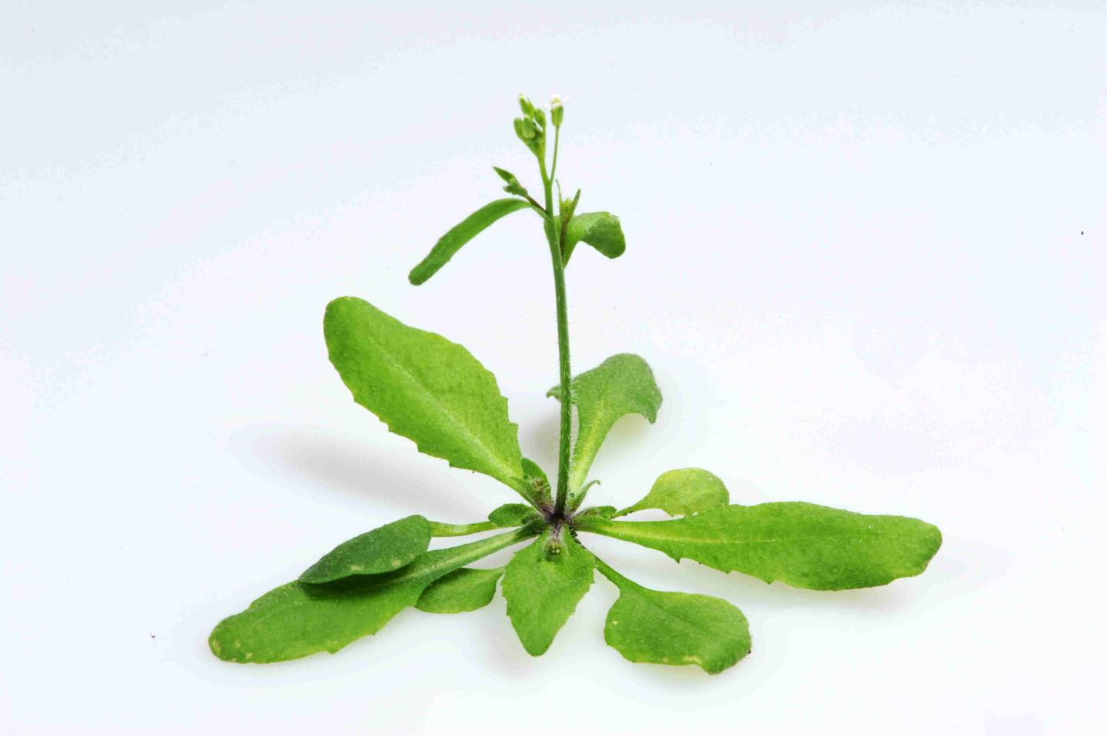
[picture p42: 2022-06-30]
ONE-PIX_soft/doc/Single Pixel Imaging tutorial/arabidopsis.jpg

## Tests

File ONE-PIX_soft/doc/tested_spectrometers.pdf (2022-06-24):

model | Tradmark
FLAME | Ocean Insigth
AvaSpec-Mini2048CL | Avantes
AvaSpec-ULS2048CL-EVO | Avantes

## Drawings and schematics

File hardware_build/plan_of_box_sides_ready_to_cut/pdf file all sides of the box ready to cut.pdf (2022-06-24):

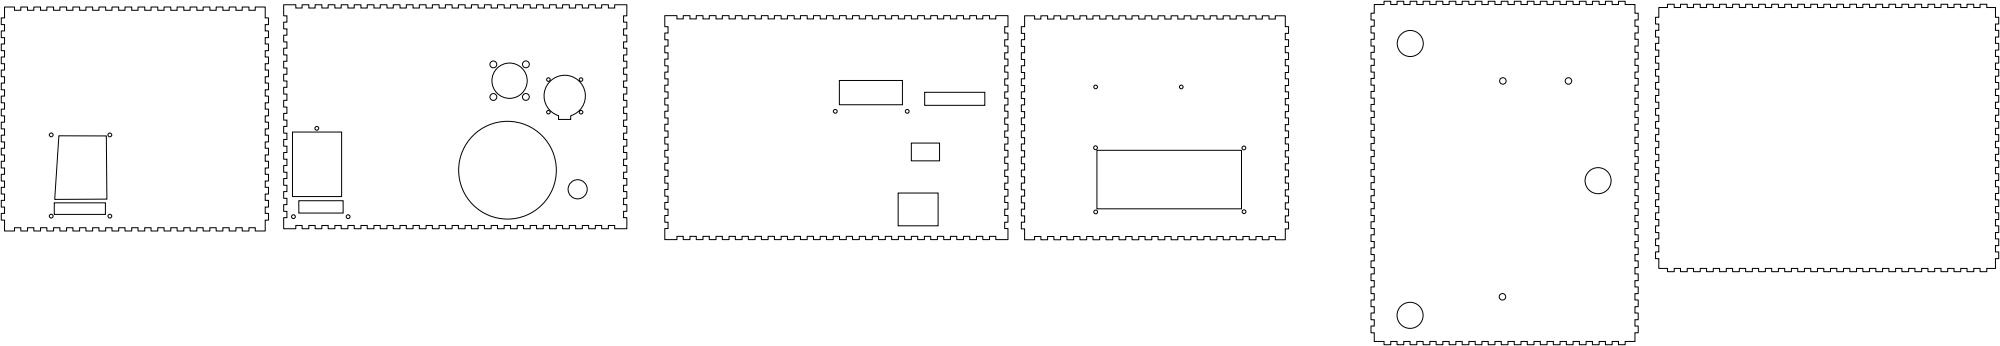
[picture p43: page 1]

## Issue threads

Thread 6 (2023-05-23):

### ISSUE TITLE
Error calculate_pattern_spectrum in DatacubeReconstructions.py

### ISSUE THREAD

**Issue by AsbroBoy** [PhotonicsOpenProjects/ONE-PIX#6]
Hello,

I have followed the procedure to add a new spectrometer to the code (Thorlabs CCS100 Spectrometer) on Windows and the Acquire spectrum in the Expert tab of the GUI app seems to work fine (I use Python 3.10) : 

![image](https://user-images.githubusercontent.com/94857159/202166045-b0dbb9a6-3821-46f0-ac66-ef18ef7a097b.png)

This is the class I've implemented for my spectrometer (correct array types for wavelengths and intensities) : 

`import os
import time
from ctypes import *

class CCS100Bridge:

    def __init__(self,integration_time_ms):
        self.integration_time_ms=integration_time_ms
        self.spec=[]
        self.DeviceName=''
        self.ccs_handle=c_int(0)
   	
    def spec_open(self):
    
        os.chdir(r"C:\Program Files\IVI Foundation\VISA\Win64\Bin")
        self.DeviceName='CCS100'
        self.spec = cdll.LoadLibrary("TLCCS_64.dll")
        self.spec.tlccs_init(b"USB0::0x1313::0x8081::M00479573::RAW", 1, 1, byref(self.ccs_handle))  
    
    def set_integration_time(self):
        integration_time = c_double(self.integration_time_ms*1e-3)
        self.spec.tlccs_setIntegrationTime(self.ccs_handle, integration_time)
        #self.integration_time_ms = integration_time.value
        #print("Integration time :", self.integration_time_ms)
        #sprint("Get 1:", self.spec.tlccs_getIntegrationTime(self.ccs_handle))
        #print("Set IT :", self.spec.tlccs_setIntegrationTime(self.ccs_handle, integration_time))
        #print("Get 2:", self.spec.tlccs_getIntegrationTime(self.ccs_handle, byref(integration_time2)))

    def get_wavelengths(self):
        self.spec.tlccs_startScan(self.ccs_handle)
        wavelengths=(c_double*3648)()
        self.spec.tlccs_getWavelengthData(self.ccs_handle, 0, byref(wavelengths), c_void_p(None), c_void_p(None))
        wavelengths_float = [float(i) for i in wavelengths]
        return wavelengths_float
    
    def get_intensities(self):
        intensities=(c_double*3648)()
        self.spec.tlccs_getScanData(self.ccs_handle, byref(intensities))
        intensities_float = [float(i) for i in intensities]
        return intensities_float
    
    def spec_close(self):
        self.spec.tlccs_close(self.ccs_handle)
`

However, when trying to acquire Hypercube in Simple mode, I obtain this error : 

![image](https://user-images.githubusercontent.com/94857159/202167203-5885fef9-0021-499d-8db5-e7a580e0278f.png)

Furthermore, when trying to acquire Hypercube in Expert mode, I obtain this error : 

![image](https://user-images.githubusercontent.com/94857159/202167453-36d96e04-60ce-4393-af60-2930316e3238.png)

Do I need to modify/add something else in the original code ?

Thanks for your help !

**Comment by PhotonicsOpenProjects** [comment]
Hey, 

Glad to hear that you were able to add easily a new class of spectrometers. When everything will be fixed and if you want to, you could push that new class so that other users could enjoy it.

Regarding your bugs, I suspect a problem with changing the integration time settings in your new class.

Can you for example send a screenshot of spectra measured simply with the GUI with several integration times, please?

Mathieu

**Comment by AsbroBoy** [comment]
Hello Mathieu, here are a few screenshots of spectra measured by GUI with the fiber pointing at a green light source (spectra change as I modify the integration times). 
Really don't know why I get problems while trying to acquire hypercube.

![image](https://user-images.githubusercontent.com/94857159/203535076-1d9489e4-dc07-465d-8112-a41f271bc139.png)

![image](https://user-images.githubusercontent.com/94857159/203535147-89b3c8f6-32fb-47d6-8251-f86af068fc06.png)

![image](https://user-images.githubusercontent.com/94857159/203534959-9bd72387-0fae-4c71-855b-02f32b336cb4.png)

**Comment by PhotonicsOpenProjects** [comment]
OK, that sounds pretty good in terms of integration times. Two things could cause this error. Firstly, if the problem comes from the duration of the spectrometer/computer communications which would be too long with this model of spectrometer and which would not ensure a sufficiently large number of measurements per projected pattern and thus an inability to measure hypercubes.
For this first option, I do not necessarily have a solution in the immediate future.
On the other hand, I have the impression that your spectra are normalised between 0 and 1 and the current scripts consider rather maximum measured intensities of the order of 65000 counts.
In your CS100 spectrometer class, try to obtain intensities between 0 and 65000 either by removing this normalization or by a direct multiplication.
